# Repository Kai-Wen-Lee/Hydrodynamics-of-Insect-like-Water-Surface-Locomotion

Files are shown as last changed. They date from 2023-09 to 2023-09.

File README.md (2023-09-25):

# Hydrodynamics of Insect like Water Surface Locomotion
 Repository for the Experimental Rig of IP: Design of an experimental set-up for research into the hydrodynamics of insect-like water surface locomotion
 
 - Individual Project Author:             James Maybey   (jdm1g20@soton.ac.uk)
 - PIC for Assembly of Experimental Rig:  Kai            (kwl1y19@soton.ac.uk)
 - Supervisor:                            Swathi Krishna (s.b.krishna@soton.ac.uk)

Current status:
 - Experimental rig nearing completion

Future work:
 1. Find better approach to achieve sinusoidal motion
 2. Fabricate additional 'platform' to ensure outer rod is straight
 3. Swap flexible couplers for solid couplers

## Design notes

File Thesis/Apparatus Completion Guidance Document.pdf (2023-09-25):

## Honeybee surface locomotion flapping arm apparatus:

This document is to help guide the completion of the IP Project Apparatus I designed and

commenced manufacturing. This will outline the remaining tasks and machining, required

components and assembly order.

The creation of this document has flagged up several issues I was not yet aware of, and

was additionally made in haste as to try not delay progress any further. If any questions

arise you feel I can help with, I can try my best to assist. Contact me with the details

below:

James Maybey, Student Email: jdm1g20@soton.ac.uk, (email or teams),

Personal email: jamesmaybey@hotmail.co.uk

I do not have all the details of these tasks figured out, and they will likely require personal

judgement to resolve.

Reading the Assembly order may help understand how all the components were intended to

fit together.

List of components (Before additional work):

- 2 x stepper motors (STM-23S-3RE)
- 2 x Serial adapter/data converter (ES-U-3001-M)
- 1 x Ruland Jaw Coupler Set (10mm bore Jaw 33mm Outer Diameter, 12mm bore Jaw

33mm ODs, 33mm OD rubber spacer)

- 1 x Small pulley 12-tooth (bore at 6.5mm needs fixing method added – set screw?)
- 1 x large pulley 48-tooth with 1 x locking bush 30mm Inner Diameter
- 1 x Toothed belt
- 1 x Plywood mounting board
- Inner shaft (10mm Diameter)
- Outer Shaft (30mm outer diameter -NEEDS CHANGE-, 24 inner diameter) w/ welded

additional mounting cylinder (50mm OD, 4 x M6 mounting holes)

- Mechanism block (Aluminium)
- Wing axle w/ wire slot
- Axle retention ring/cap (21mm ID, mm OD)
- Axle-to-sensor backplate coupler/sleeve (21mm ID, mm OD)
- Sensor back plate (NEEDS ALTERATION/REMANUFACTURING)
- 2 x ball bearings (10mm ID, 26mm OD)
- 1 x ATI NANO17 IP68 (using 3 x M2 screw mounting, no alignment pins)
- 1 x acrylic wing (34mm x 107mm)
- 1 x 3D printed wing adapter/holder (may need redesign/printing)
- 1 x 16-tooth bevel gear (10mm ID, + set screw)
- 1 x 24-tooth bevel gear (21mm ID, + set screw)

- 1 x flange shaft bearing (30mm Bore)
- 1 x Aluminium shaft flange plate (Mounts to Outer shaft with 4 x M6)
- 1 x gearbox Mounting plate (Mounts to gearbox with 4 x M5)
- 4 x Metal Standoffs/spacers (mounts the flange plate and gearbox mounting plate

together with M6)

- 1x Gearbox compatible with stepper motor
- + Fixings

One of the first things that needs to be done is check the mounting of the gears in

respect to the holes bored in the block. The spacing was based on the distances

specified by the manufacturers however I never got to test these aligned in the received

components. If these do not align the block or gears may need

redesigning/manufacturing and this could be a huge problem and setback. The gears

may want a few millimetres taken off the base anyway to stop them being positioned

against the aluminium block and increasing friction.

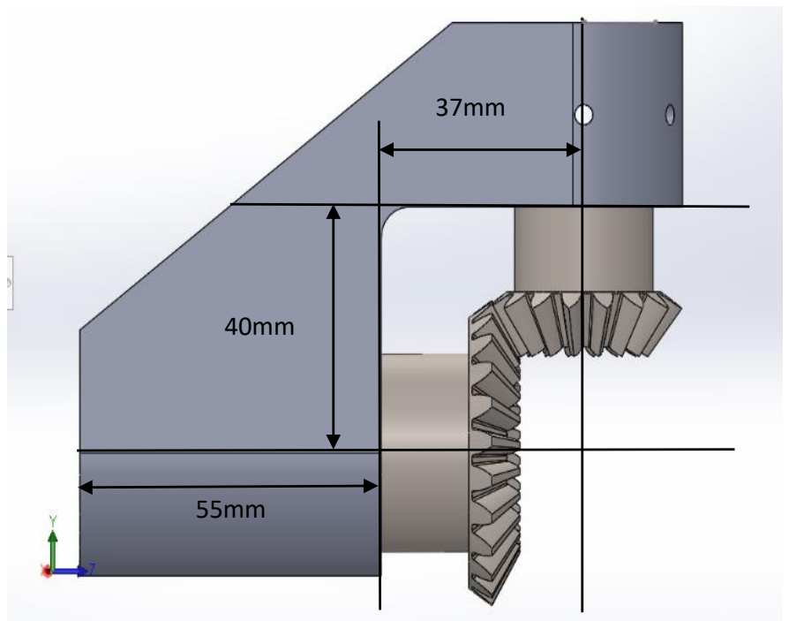
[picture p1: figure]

Tasks to be completed:

- 1. Collect Components from EDMC (if not already done so) – EDMC was to make

the bores of the ‘24-tooth bevel gear’, ‘axle retention ring’ and ‘axle-to-sensor

plate coupler/sleeve’ to 21mm, this is to ensure the 20.1mm sensor can pass

through inside. The EDMC was also supposed to machine the inner diameters of

the Outer shaft to 26mm (from 24mm) to a minimum depth of 8mm on both

ends (this is to hold the alignment bearings)

- 2. The outer shaft OD needs to be reduced on a lathe from 30mm diameter

downwards until it can pass into the 30mm bore of the flange bearing, this is

only required on the longer length of the shaft below the additional welding

piece.

- 3. Get a 700mm length of aluminium 10mm diameter rod (inner shaft) from the

EDMC, may require a material order as they did not have stock when I checked.

This can then be cut to final length during assembly (expected closer to 640mm).

The inner shaft may need its diameter reduced to pass through the 10mm ID

bores of the Alignment bearings and the 16-tooth bevel gear. (Making sure the

10mm Ruland jaw will still have a solid connection/grip)

- 4. The serial adapters need to be positioned and mounted appropriately.

(availability of this part in the labs is questionable so ordering the component

may be necessary). Wiring also needs to be arranged with wires long enough to

run into the tank and between components (Electronics workshop on highfield

campus can help with this).

- 5. The Stepper Motors need to be coded for a sinusoidal motion with 1Hz

frequency resulting in angles of attack between ±45°. For further motion

requirements, discuss with Swathi Krishna. (Wiring also needs to be arranged)

(Ben may be able to assist with Coding)

- 6. A mounting frame needs designing and creating with the available lengths in

Building 185 that is compatible with the Tank and mounting plate and positions

the wing at a suitable depth.

- 7. Alter/Remanufacture/Redesign Sensor Back plate, The current back plate is

compatible with the standard Nano17 model however the IP68 submergible

model has different mounting arrangements and so this needs a new piece or

alterations. An example suitable design has been provided. This can be used if

deemed suitable.

- 8. The 3D printed Wing adapter that holds the acrylic wing may require

redesigning and reprinting if the mounting holes for M2 screws do not align with

new sensor and also aren’t positioned for easy assembly.

- 9. Check wing size gives an estimate torque reading that does not exceed the

rating of the sensor. If not Lasercut new wing to new chosen design – Discuss

with Swathi Krishna.

- 10. If alignment bearings don’t stay in the outer shaft with a pressure fit, add an

additional method of retention.

- 11. Where deemed applicable and possible add countersinks if time permits.
- 12. During assembly it may be found the ‘Axle coupler/sleeve’ needs to be

machined to a shorter length if the bevel gear and coupler interact.

- 13. Make the jaw couplers support axial load

- 14. Add set screw to small pulley/ make shaft extension+coupler

Task 1:

‘Collect Components from EDMC (if not already done so) – EDMC was to make the bores of

the ‘24-tooth bevel gear’, ‘axle retention ring’ and ‘axle-to-sensor plate coupler/sleeve’ to

21mm, this is to ensure the 20.1mm sensor can pass through inside (aluminium block has

20.5mm hole). The EDMC was also supposed to machine the inner diameters of the Outer

shaft to 26mm (from 24mm) to a minimum depth of 8mm on both ends (this is to hold the

alignment bearings)’

Technical drawings shown below highlighting the mentioned changes referred to.

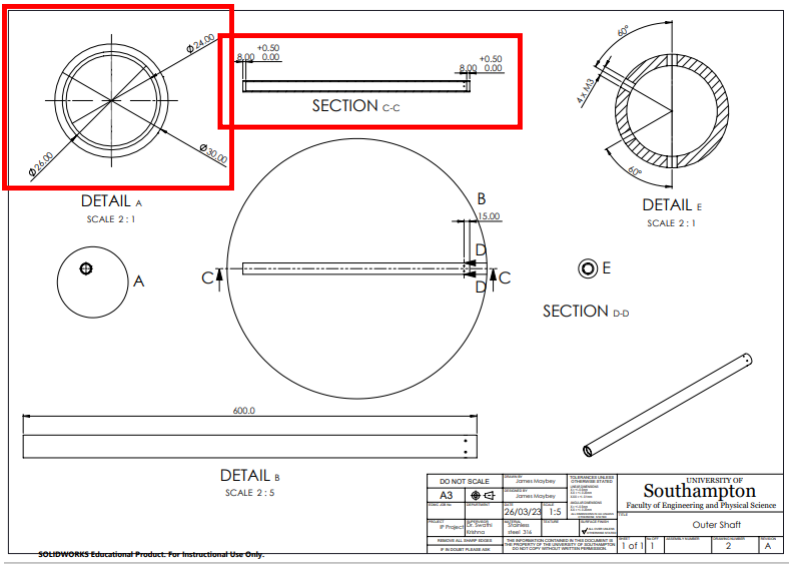
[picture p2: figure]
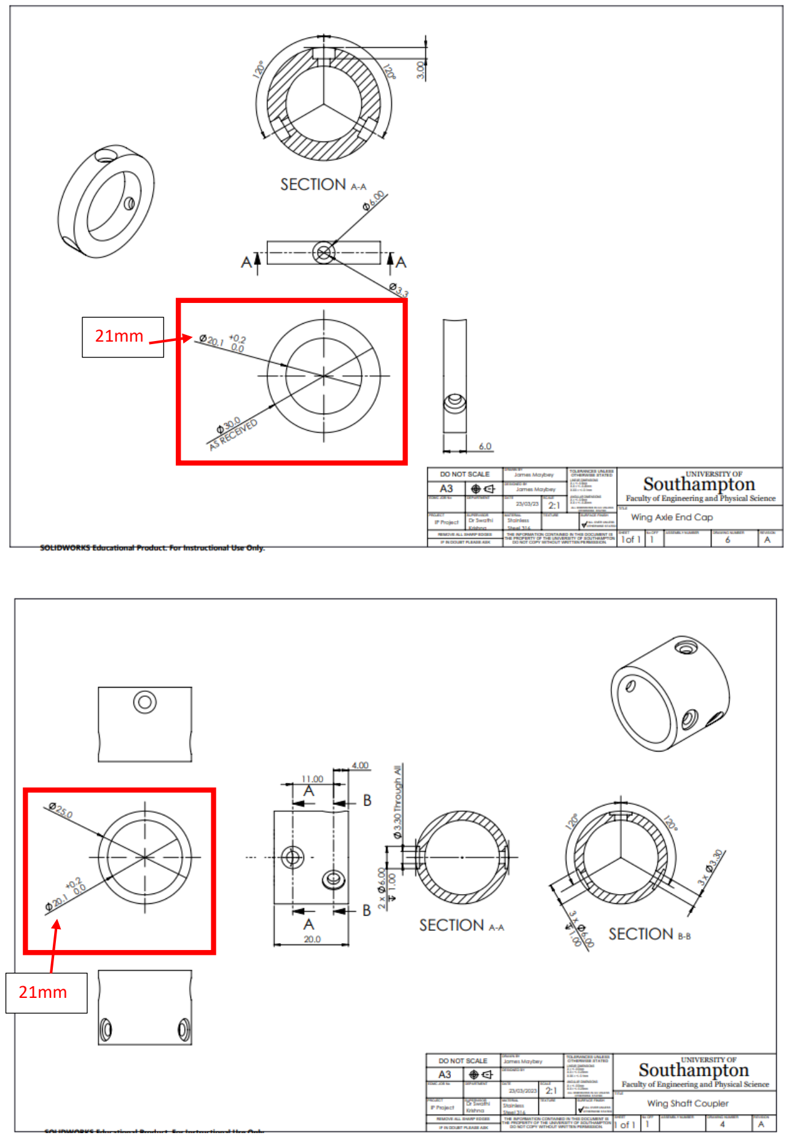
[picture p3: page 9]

21mm

21mm

Task 2:

‘The outer shaft OD needs to be reduced on a lathe from 30mm diameter downwards until

it can pass into the 30mm bore of the flange bearing, this is only required on the longer

length of the shaft below the additional welding piece.’

Technical drawings of Outer shaft assembly and flange bearing with areas of change

highlighted.

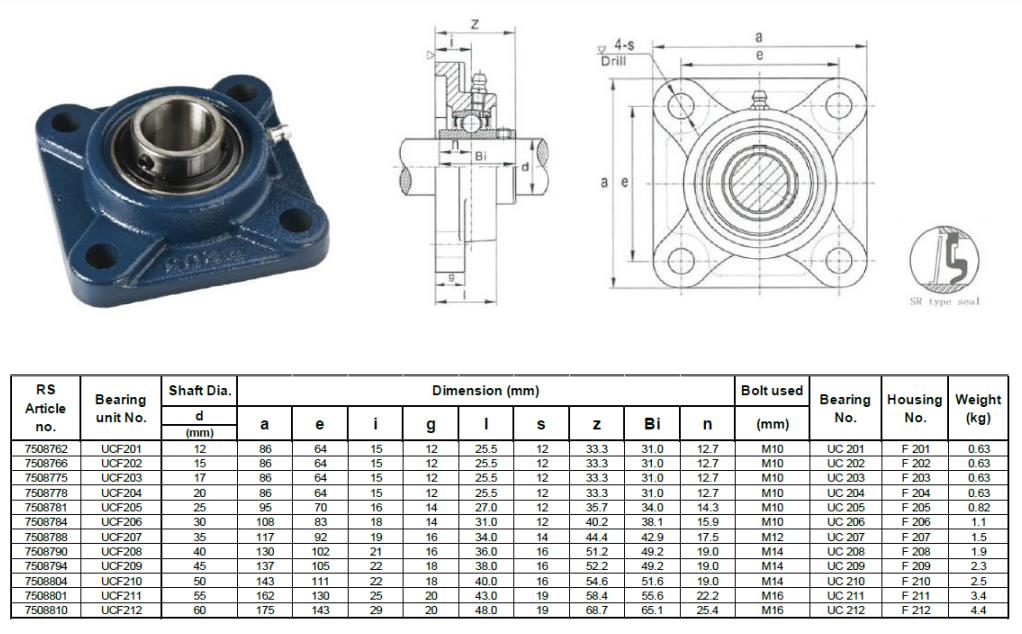
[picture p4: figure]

^^^Using 30mm shaft diameter size (d)^^^

Task 3:

‘Get a 700mm length of aluminium 10mm diameter rod (inner shaft) from the EDMC, may

require a material order as they did not have stock when I checked. This can then be cut to

final length during assembly (expected closer to 640mm). The inner shaft may need its

diameter reduced to pass through the 10mm ID bores of the Alignment bearings and the 16-

tooth bevel gear. (Making sure the 10mm Ruland jaw will still have a solid connection/grip)’

Drawings of inner shaft and alignment bearings assembly.

Rough estimate

Task 4:

‘The serial adapters need to be positioned and mounted appropriately. (availability of this

part in the labs is questionable so ordering the component may be necessary). Wiring also

needs to be arranged with wires long enough to run into the tank and between components

(Electronics workshop on highfield campus can help with this).’

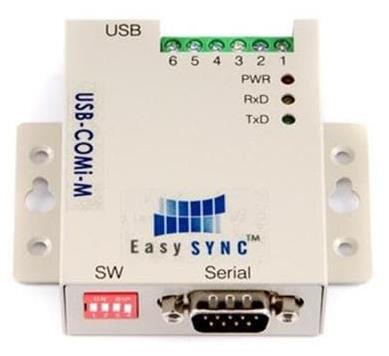
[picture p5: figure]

ES-U-3001-M USB-to-Serial data converter

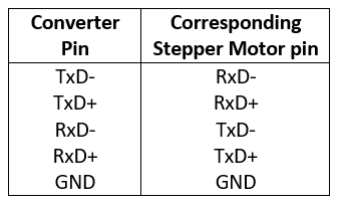
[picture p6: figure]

Wiring guide between converter and stepper motor

The switches on the converter should display S1,2 and 4 ON and S2 OFF, using this table

below as guide.

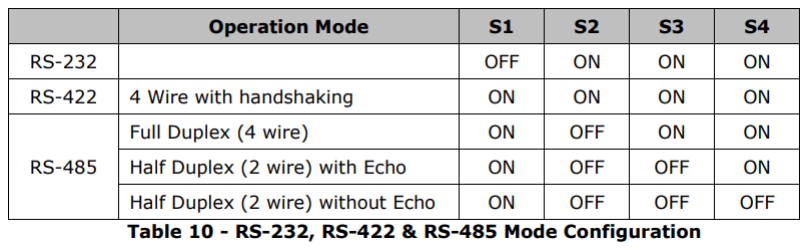
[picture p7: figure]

Task 5:

‘The Stepper Motors need to be coded for a sinusoidal motion with 1Hz frequency resulting

in angles of attack between ±45°. For further motion requirements, discuss with Swathi

Krishna. (Wiring also needs to be arranged) (Ben may be able to assist with Coding)’

Link to control codes and documentation

Useful links for setup and coding:

https://appliedmotion.s3.amazonaws.com/920-0020F_STM23_24_S_Q_QuickSetup.pdf

https://www.applied-motion.com/s/product/integrated-

drivemotorstm23s3re/01t5i000000xylkAAA (https://www.applied-motion.com/s/product/integrated-drivemotorstm23s3re/01t5i000000xylkAAA)

https://appliedmotion.s3.amazonaws.com/Host-Command-Reference_920-0002W_0.pdf

Task 6:

‘A mounting frame needs designing and creating with the available lengths in Building 185

that is compatible with the Tank and mounting plate and positions the wing at a suitable

depth.’

Mounting board technical drawing and example image of mounting, can also look at Ben’s

cyclorotor for example.

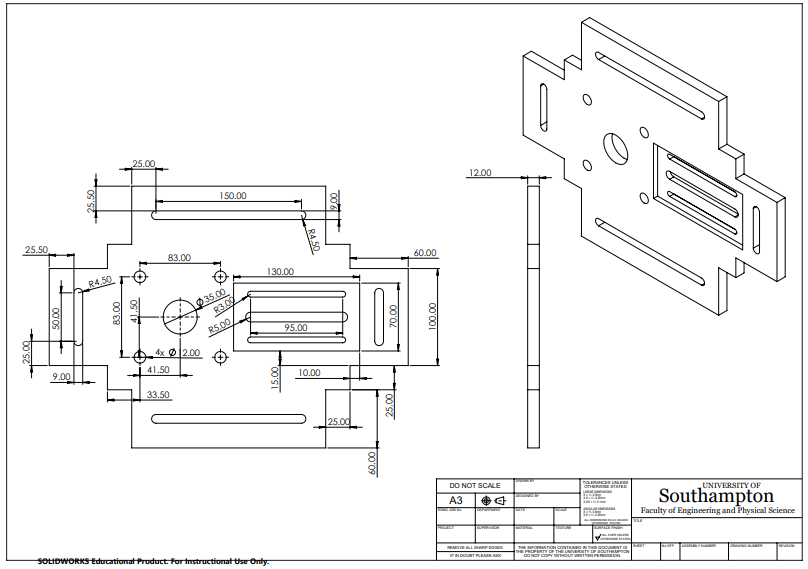
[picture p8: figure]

Mounting board dimensions, Suitable for M8 bolts to secure to framework

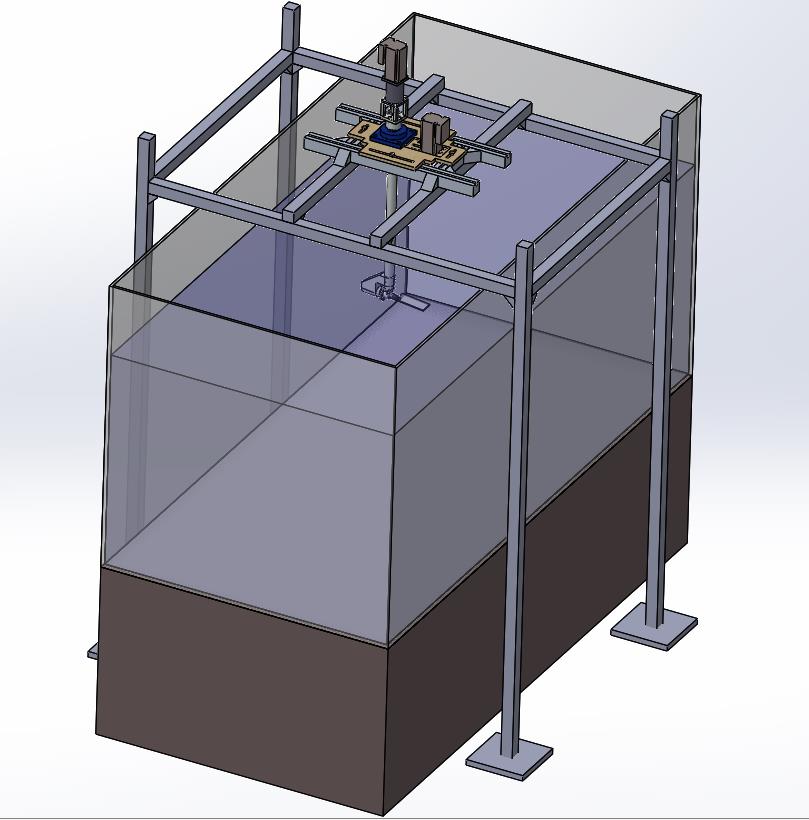
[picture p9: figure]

Example mount structure, does not need to be followed

Task 7:

‘Alter/Remanufacture/Redesign Sensor Back plate, The current back plate is compatible

with the standard Nano17 model however the IP68 submergible model has different

mounting arrangements and so this needs a new piece or alterations. An example suitable

design has been provided. This can be used if deemed suitable.’

Existing plate (photo of final look, +countersinks, -thread in side M3 holes)(drawings from

EDMC order of existing plate):

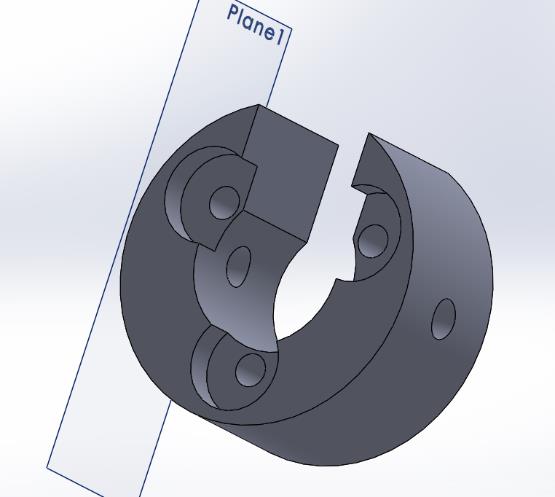
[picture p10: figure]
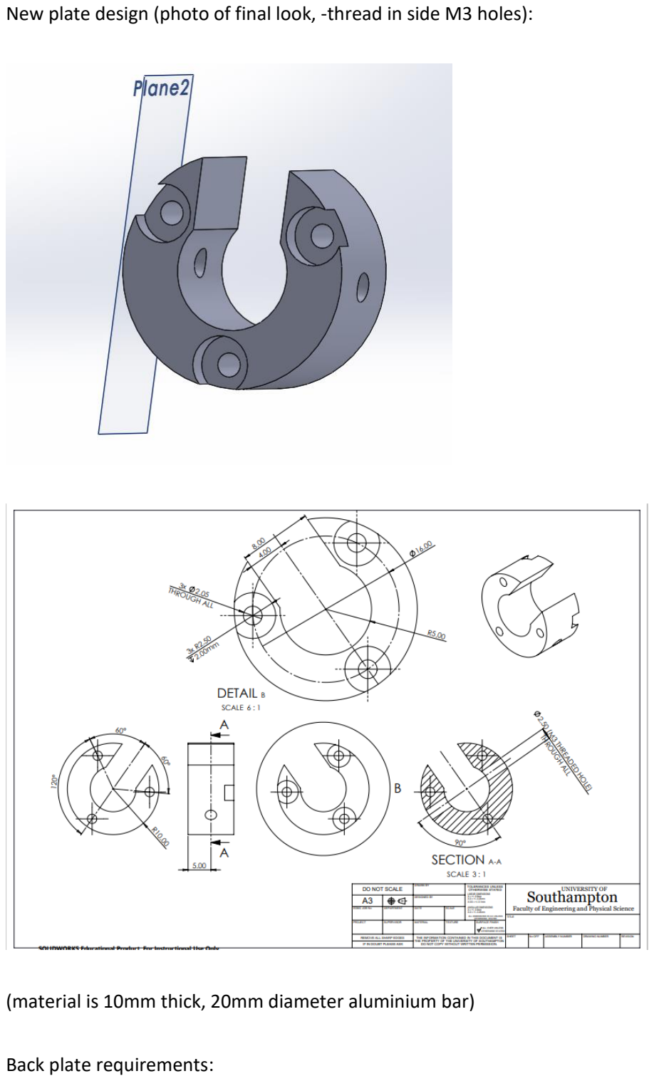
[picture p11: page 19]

New plate design (photo of final look, -thread in side M3 holes):

(material is 10mm thick, 20mm diameter aluminium bar)

Back plate requirements:

Diameter ~20mm, ATI sensor wire slot and hole suitable for the axial cable, 3x M2 clearance

mounting/interface holes, 2 x Connecting M3 threaded holes for sensor-to-axle coupler,

Countersinks to keep screw head flush or beneath outerface.

Reducing the backplate to 9.5mm length instead of 10mm allows for further assembly

tolerance.

CONSIDER SCREW HEAD SIZE, IF THEY EXCEED OVER THE EDGE IN THE COUNTERSINKS, THE

PART MAY NOT FIT INSIDE THE COUPLER, SOLUTIONS: SCREW HEADS COULD BE

MACHINED AWAY, OR DESIGN REWORKED

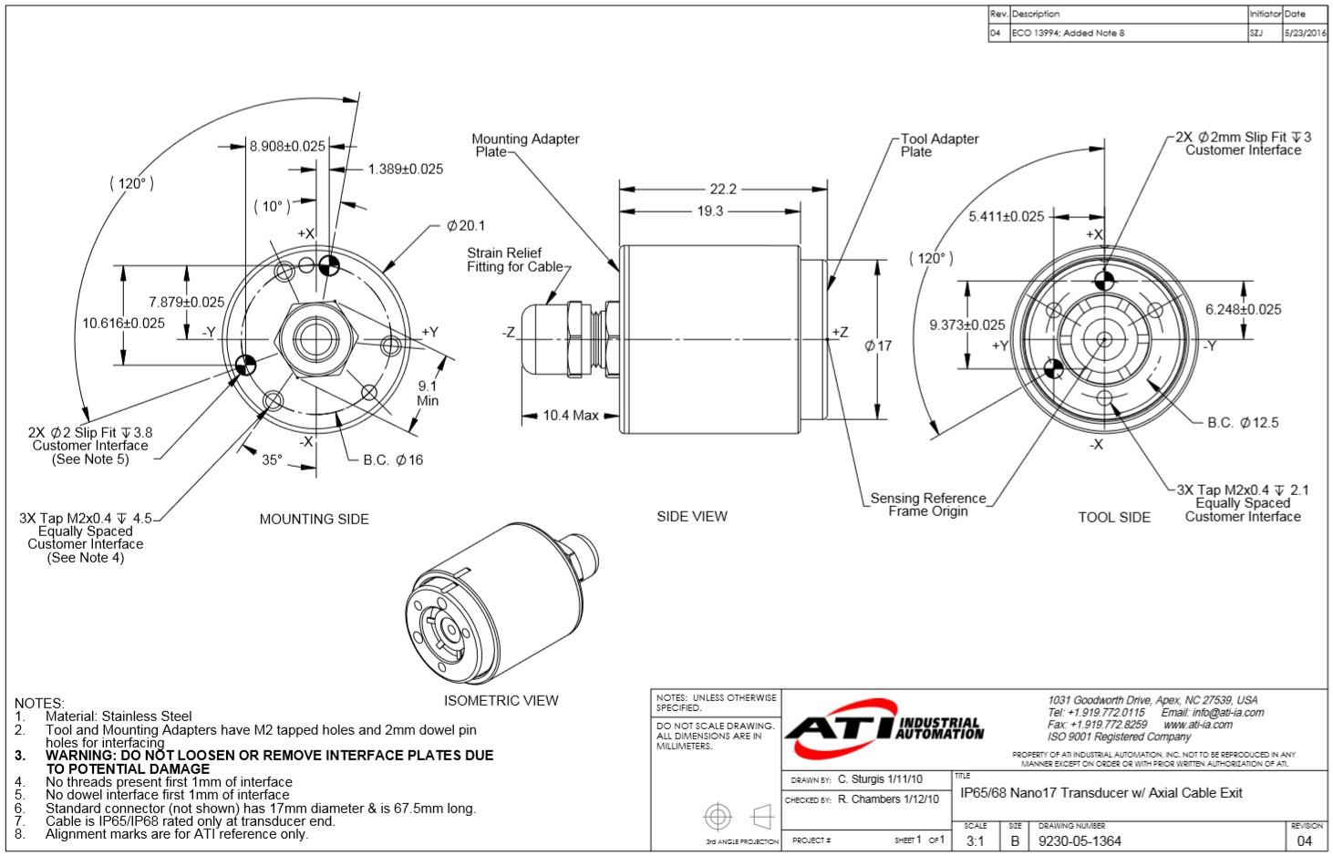
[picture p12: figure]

Task 8:

‘The 3D printed Wing adapter that holds the acrylic wing may require redesigning and

reprinting if the mounting holes for M2 screws do not align with new sensor and also aren’t

positioned for easy assembly.’

Current 3D print problems:

Difficulty screwing in 3x M2 fixing screws

Fixing interface shown below

Requirements:

3x M2 screw interface clearance holes with countersinks, centres on 12.5mm circular

arrangement 120 Degrees apart

Two pronged forks with semi circular profile to hold plastic wing (current design uses

2.05mm max thickness prongs with 10mm length.)

Task 9:

‘Check wing size gives an estimate torque reading that does not exceed the rating of the

sensor. If not Lasercut new wing to new chosen design – Discuss with Swathi Krishna.’

Swathi was to check the calculations to make sure the torque on the wing did not exceed

the sensors max torque. If change is required arrange measurements with Swathi and laser

cut replacement.

Wing plate should be positioned with the forks at a quarter chord length from the leading

edge, shown below.

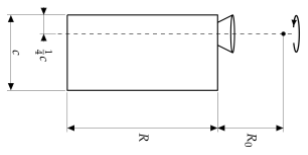
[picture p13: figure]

Current wing size 34mmx107mm, 3mm thickness clear acrylic

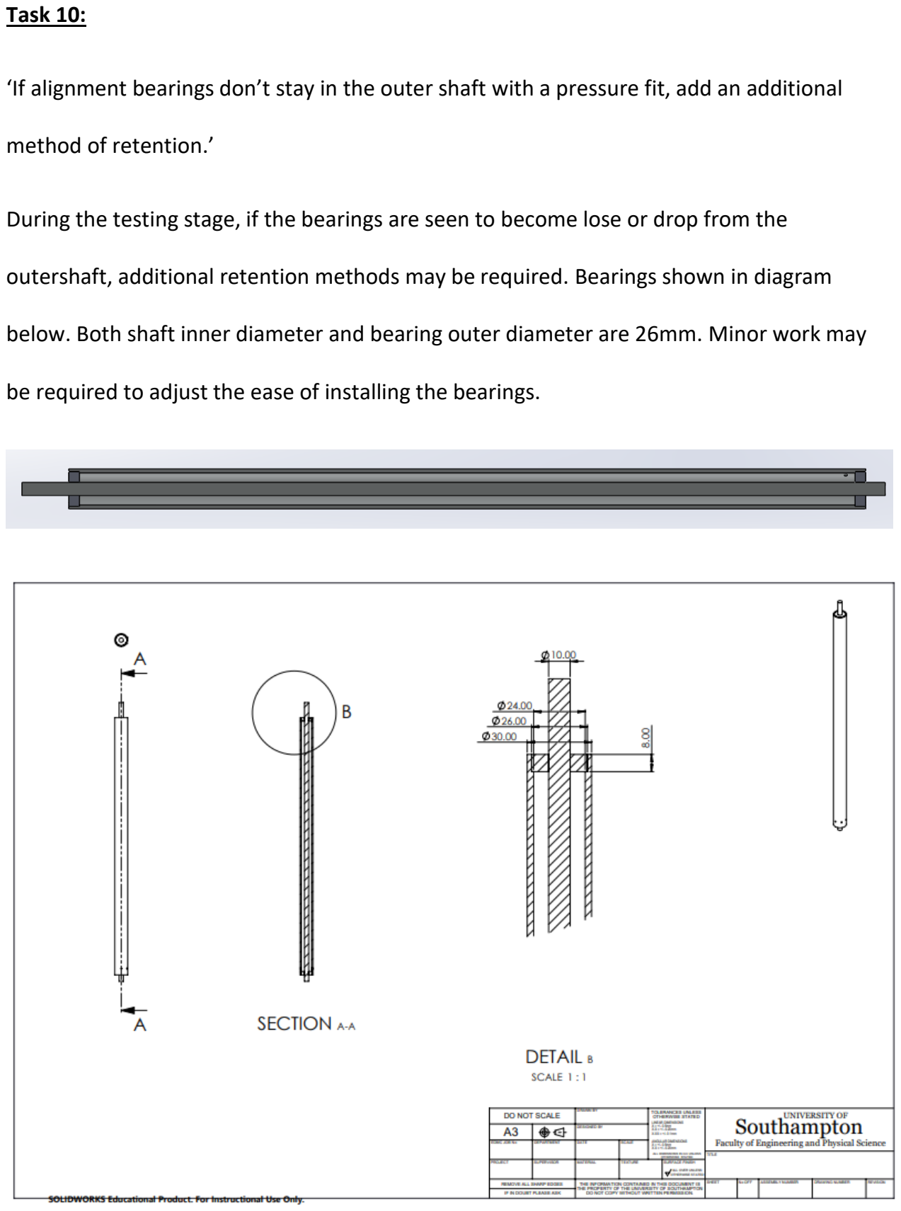
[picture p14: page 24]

Task 10:

‘If alignment bearings don’t stay in the outer shaft with a pressure fit, add an additional

method of retention.’

During the testing stage, if the bearings are seen to become lose or drop from the

outershaft, additional retention methods may be required. Bearings shown in diagram

below. Both shaft inner diameter and bearing outer diameter are 26mm. Minor work may

be required to adjust the ease of installing the bearings.

Task 11:

‘Where deemed applicable and possible add countersinks if time permits.’

Countersinks can be added to components if size and material width permits, e.g axle

retention ring.

WARNING: With the inner bore increased to 21mm by the EDMC, the remaining material

is reduced for counterbore depth

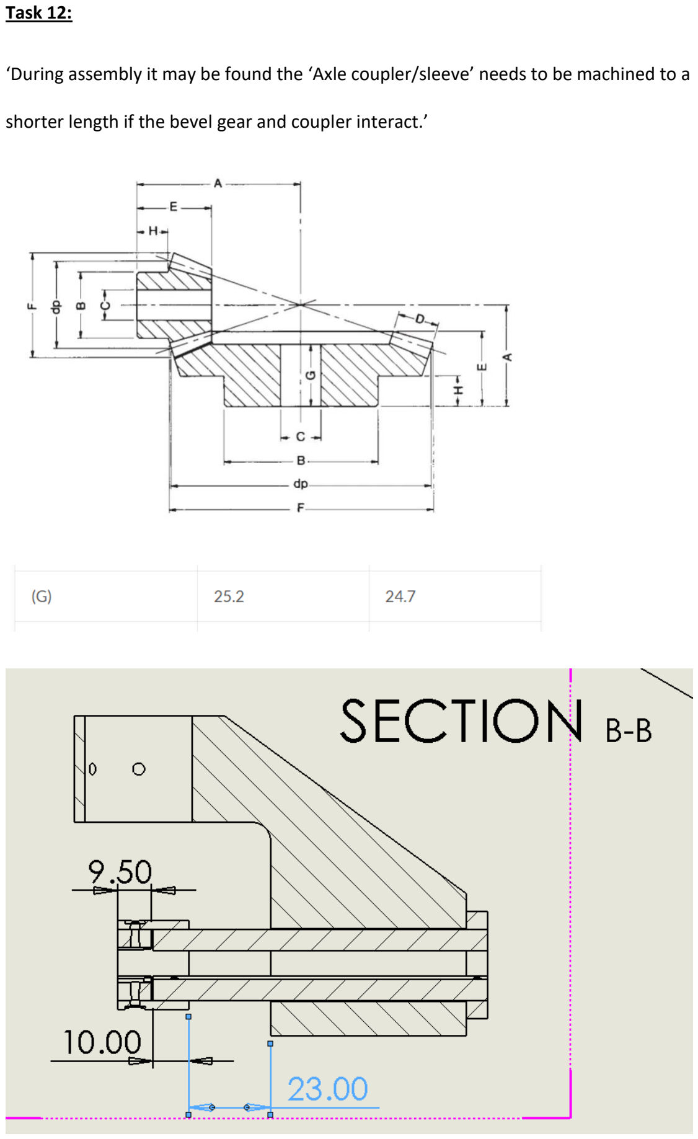
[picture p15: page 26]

Task 12:

‘During assembly it may be found the ‘Axle coupler/sleeve’ needs to be machined to a

shorter length if the bevel gear and coupler interact.’

Design currently leaves 23mm space for 24.7mm long gear (Measurement specified by

manufacturers site, Not measured from received component).

There are 3 options to change this:

- Machine the Gears front face (where the teeth are) back, however make sure to try

not to interfere with gear meshing

- Machine the coupler back however this will start to near the 3x M3 clearance holes
- Produce a new, longer, axle that will increase this space (Simplest fix but most

effort and cost)

Task 13:

‘Make the jaw couplers support axial load’

I was made aware that there was a way to further manufacture onto the jaw coupler to

allow the coupler to support load axially (to not pull apart at the rubber spacer). I am unsure

whether this will be required as the attached driving gear will fall against the 2nd gear and

this may permit operation.

I am not sure how this change to the coupler is done as I never got round to investigating

myself but I believe I was instructed to speak to Building 185 Technician Sam Harper.

Task 13:

‘14. Add set screw to small pulley/ make shaft extension+coupler’

Due to the bolts that hold the flange bearing in place, the pulley may need to be positioned

lower on the outer shaft. To achieve correct alignment, the small pulley may need to be

fixed to another shaft that couples to the motor. The motor has 6.35mm output shaft

diameter whilst the pulley has a 6.5mm drilled bore.

By adding a 1 or 2mm set screw to the neck of the small (12-tooth) pulley, it can be fixed

to a 6.5mm shaft and then coupled to the motor. This Coupler will need to be bought or

made.

Assembly:

Step No. | Step | Components involved | Instructions
1 | Fix the outer shaft | Welded outer shaft subassembly, Mounting frame, Plywood mounting board, Flange bearing | Fix the flange bearing to the board and the board to the frame with M10 and M8 bolts, then push the outer shaft through the bearing and tighten set screws.
2 | Insert inner shaft and bearings | Inner shaft, alignment bearings x2, outer shaft | Push the inner shaft down the outer shaft and place the alignment bearings over the inner shaft and into the ends of the outer shaft
3 | Fix the pulley system | Large pulley, small pulley, locking bush, pulley belt, stepper motor | Slide the large pulley and bush onto the outer shaft from underneath and tighten the set screws to fix, then place motor onto the board and use set screw to fix the small pulley onto the shaft, then use 4 M4 machine screws to bolt the motor into position whilst tightening the belt in place.
4 | Fix the second motor | Gearbox, motor, gearbox plate, outer shaft plate, standoffs x4, Ruland jaw coupler | Bolt the shaft plate onto the welded sleeve on the top of the outer shaft using 4 M6 bolts, then secure the 4 standoffs to this plate with 4 more M6 bolts, secure the motor to the gearbox using 4 M5 machine screws and then bolt the gearbox to its plate with 4 M5 bolts, this plate can then lastly be secured to the standoffs with M6 bolts at the same time the Ruland jaw coupler is aligned and fixed to the inner shaft and gearbox output
5 | Create the gear sub assembly | Mechanism block, retention ring, Nano17, sensor back plate, 21mm bore gear, wing axle, coupling sleeve | Firstly, pass the sensor through the retention ring, mechanism block, 21mm bore gear, and coupling sleeve. Then slot the back plate over the sensors wire and fix the backplate to the back of the sensor with M2 screws, then slot the wing axle over the wire and slide into place. Then using M3 screws, fix the sleeve to the back plate and wing axle, then slot the wing axle through the gear and mechanism block and fix to the retention ring with M3s, finally tighten the 24-tooth gear’s set screw to fix into the wing axle.
6 | Fix the wing to the sensor | Wing adapter, wing plate | Glue the wing plate into position in the adapter, then screw the adapter onto the sensor using M2 screws
7 | Fix the gear sub assembly onto the outer shaft | 16-tooth driving gear | Putting the driving gear into its final position next to the driven gear allows for the assembly to be slid onto the bottom of the outer shaft and the inner shaft can pass into the driving gear whilst the outer shaft stays in the mechanism block, the set screw can then be tightened, fixing the gear, and the 4 M3 machine screws can be used to fix the mechanism block onto the outer shaft
8 | Mount the apparatus | Testing environment | The mounting frame can then be fixed to the existing frame above the tanks using right-angled brackets
9 | Fix the electronics | Wire connections, signal converter (serial adapter) | The wiring can then be implemented, from power source to motors and from signal generator to the converters and then also to the motors. The sensor wire can also then be connected into the reading device, signal converters can be screwed onto the wooden board for fixing if space permits.

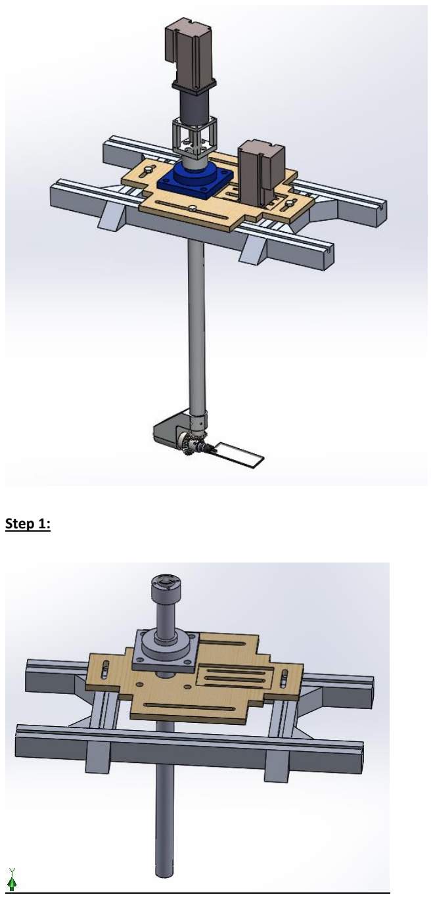
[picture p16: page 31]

Step 1:

Step 2:

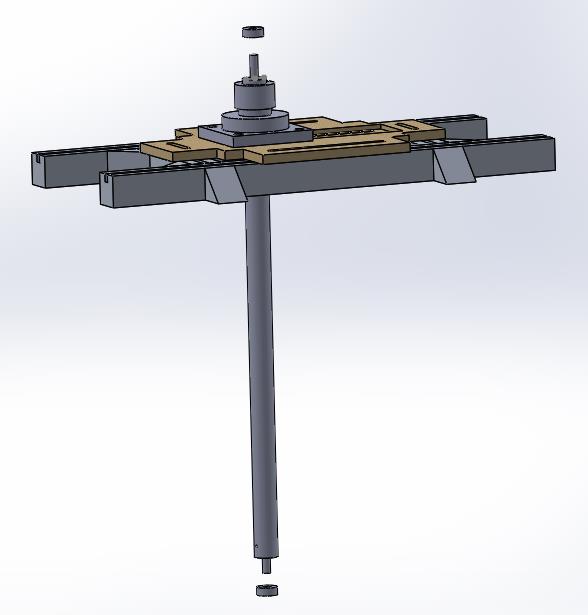
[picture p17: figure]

Step 3:

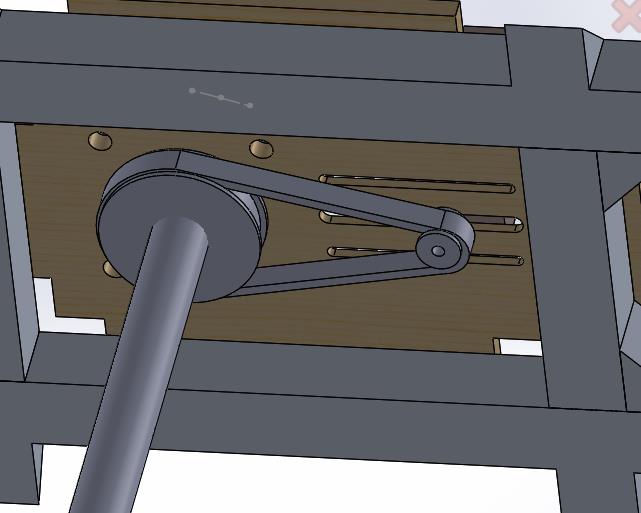
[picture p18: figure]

This step does not show the additional shaft/coupler that will likely be needed. Image

shows how belt is close to the flange bearing mounting holes.

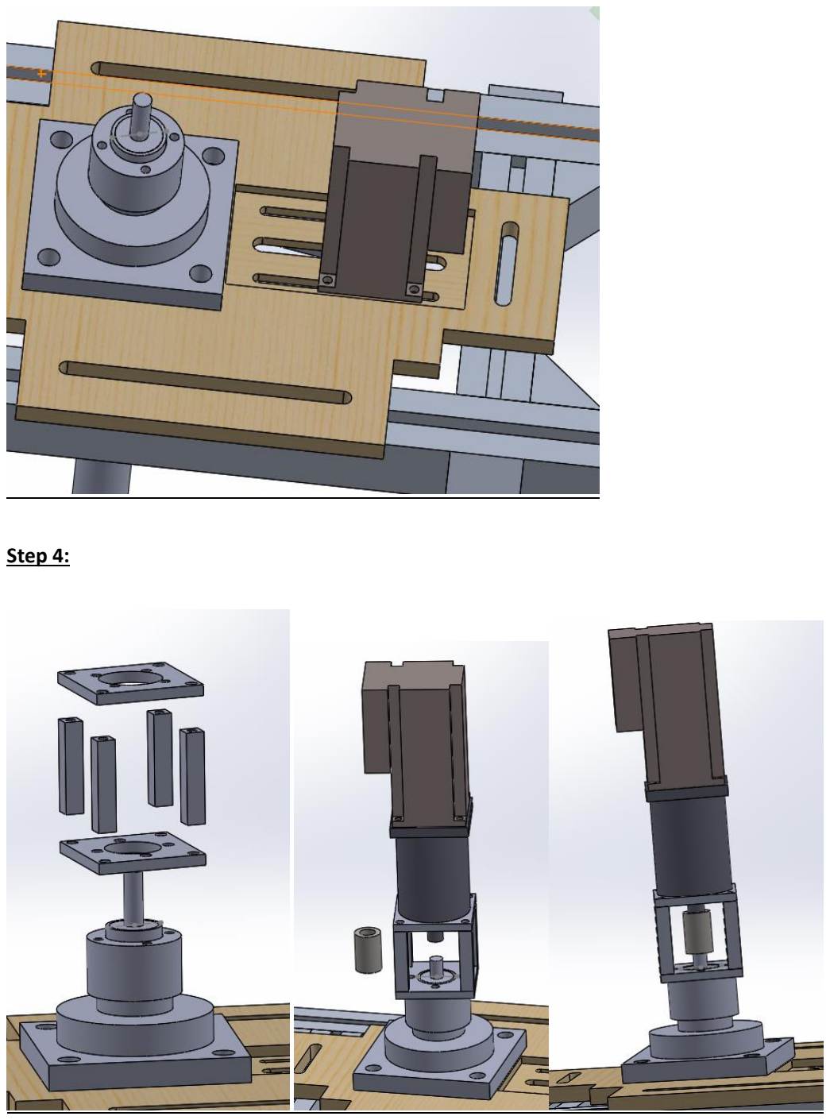
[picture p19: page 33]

Step 4:

Step 5:

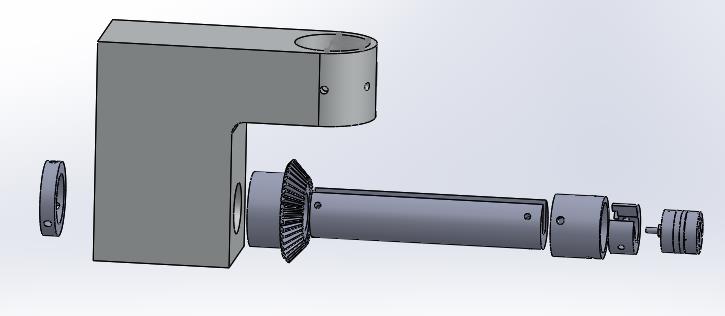
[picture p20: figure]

Due to the sensors axial cable, it will need to pass through the bores of the end ring,

aluminium block,24-tooth gear, and coupler

Step 6:

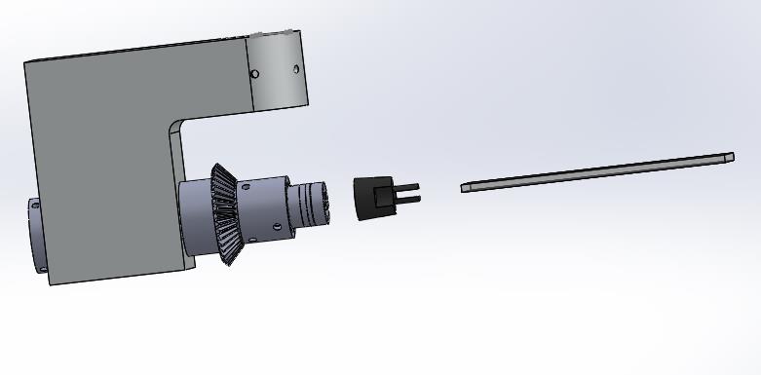
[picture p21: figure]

(Gears not accurate – shown gear corresponds to 24-tooth gear)

Step 7:

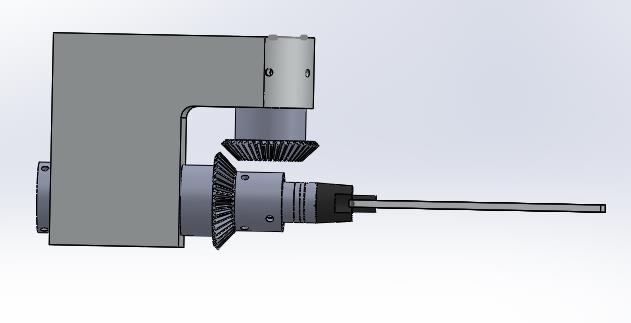
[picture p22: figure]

(Gears not accurate – New gear in photo corresponds to 16-tooth gear)

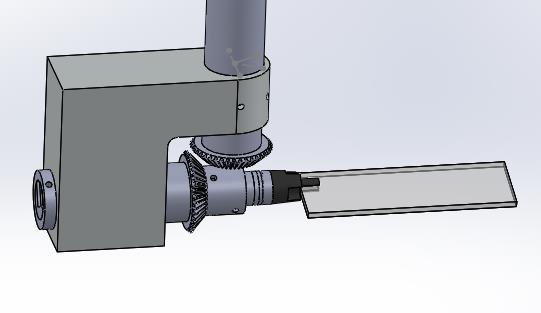
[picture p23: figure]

Slide both parts pre-positioned up onto the bottom of the outer and inner shaft

Step 8:

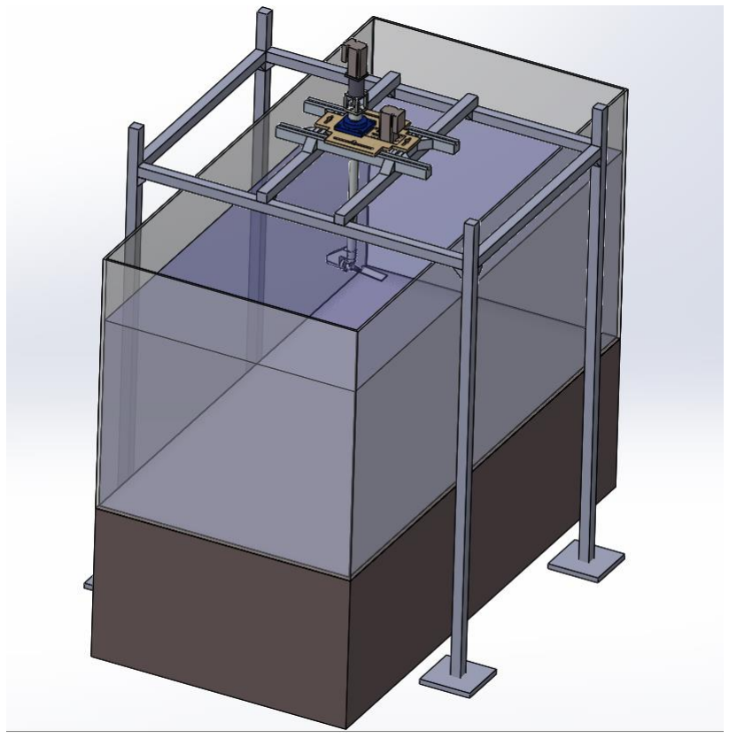
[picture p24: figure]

Step 9:

Fix Electronics

More Useful links:

https://www.applied-motion.com/s/product/detail/01t5i000000xylkAAA?name=STM23S-

3RE-NEMA-23-Integrated-Drive-Motor-w-Encoder (https://www.applied-motion.com/s/product/detail/01t5i000000xylkAAA) – Stepper motor

https://simplybearings.co.uk/shop/p20194084/P12-5M-15F-5mm-Pitch-12-Tooth-Flanged-

HTD-Type-Steel-Timing-Pulley-for-15mm-Wide-Belts/product_info.html (https://simplybearings.co.uk/shop/p20194084/P12-5M-15F-5mm-Pitch-12-Tooth-Flanged-HTD-Type-Steel-Timing-Pulley-for-15mm-Wide-Belts/product_info.html) - small pulley

https://simplybearings.co.uk/shop/p671275/HTD425-15-85-Major-Brand-Synchronous-Belt-

15mm-Wide-5mm-Pitch-85-Teeth/product_info.html (https://simplybearings.co.uk/shop/p671275/HTD425-15-85-Major-Brand-Synchronous-Belt-15mm-Wide-5mm-Pitch-85-Teeth/product_info.html) - Pulley belt

https://simplybearings.co.uk/shop/p20193090/TL48-5M-15F-5mm-Pitch-48-Tooth-Flanged-

HTD-Type-Steel-Taper-Bore-Timing-Pulley-for-15mm-Wide-Belts/product_info.html (https://simplybearings.co.uk/shop/p20193090/TL48-5M-15F-5mm-Pitch-48-Tooth-Flanged-HTD-Type-Steel-Taper-Bore-Timing-Pulley-for-15mm-Wide-Belts/product_info.html) - large

pulley

https://simplybearings.co.uk/shop/p552040/1210-30-Tapered-Locking-Bush-with-30mm-

Bore/product_info.html (https://simplybearings.co.uk/shop/p552040/1210-30-Tapered-Locking-Bush-with-30mm-Bore/product_info.html) -large pulley locking bush

https://uk.rs-online.com/web/p/ball-bearings/6189991 - ball bearing

https://bepltd.com/products/2-mod-1-5-ratio-16-24-teeth-precision-bevel-gears-steel-en8 -

bevel gear pair

https://uk.rs-online.com/web/p/bearing-units/7508784 - flange bearing

https://uk.rs-online.com/web/p/flexible-couplings/4231775 - 12mm gearbox jaw for

coupling

https://uk.rs-online.com/web/p/flexible-couplings/7019155 - coupling rubber spacer

https://uk.rs-online.com/web/p/flexible-couplings/4231769 - 10mm inner shaft jaw for

coupling https://motioncontrolproducts.com/media/productattach/r/e/re-planetary-gearbox.pdf -

gearbox dimensions (RE55 model for Nema 23)

https://www.ati-ia.com/products/ft/ft_models.aspx?id=Nano17+IP65%2fIP68 – ATI Nano17

IP68 Web page (useful documents for sensor found here)

https://uk.rs-online.com/web/p/standoffs/1768297 - Metal female-female standoffs

(unsure if these are the exact ones)

https://www.mouser.co.uk/ProductDetail/Connective-Peripherals/ES-U-3001-

M?qs=jotIDw4kbYV9GiEaKLbLDA%3D%3D (https://www.mouser.co.uk/ProductDetail/Connective-Peripherals/ES-U-3001-M?qs=jotIDw4kbYV9GiEaKLbLDA%3D%3D) – Serial adapter/data converter, Data sheet can

be found here

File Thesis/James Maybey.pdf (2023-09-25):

a

# Design of an experimental set-up for research into

# the hydrodynamics of insect-like water surface

# locomotion

## James Maybey

18/05/2023

## Dr. Swathi Krishna, Desmond Lim

## Word Count: 10,499

## Pages: 70

## This report is submitted in partial fulfilment of the requirements for the

## Mechanical Engineering with Automotive Engineering, Faculty of

## Engineering and Physical Sciences, University of Southampton

i

## Decleration:

I, James Maybey declare that this thesis and the work presented in it are my own and has been generated by me as the result of my own original research.

I confirm that:

1. This work was done wholly or mainly while in candidature for a degree at this University;
2. Where any part of this thesis has previously been submitted for any other qualification at this University or any other institution, this has been clearly stated;
3. Where I have consulted the published work of others, this is always clearly attributed;
4. Where I have quoted from the work of others, the source is always given. With the exception of such quotations, this thesis is entirely my own work;
5. I have acknowledged all main sources of help;
6. Where the thesis is based on work done by myself jointly with others, I have made clear exactly what was done by others and what I have contributed myself;
7. None of this work has been published before submission.

James Maybey

ii

### Acknowledgements:

I thank my supervisor Dr. Swathi Krishna for supporting my work and giving me guidance

during my project. I also am grateful for being given the opportunity to work on this

project by Dr. Krishna. I further thank Desmond Lim for offering his additional time and

support on this project. I lastly thank my Father for helping me and giving me the

motivation to continue with my work.

iii

### Abstract:

Many studies have been made over time into the motion employed by insects’ wings.

The latest motions to be studied need to be replicated and analysed by employing an

experimental apparatus. A vast number of set-ups exist with the sole purpose of

recreating the flapping motion of wings, and from these, results can be found and

implemented into robotic application. Unmanned vehicles in both air and water would

benefit greatly from the planned future research. The hydrofoiling of honeybee’s wings

will allow for a great new deal of design possibilities, with existing ideas for

implementation in drone recovery.

This paper outlines the design of an experimental piece of equipment that will allow the

modelling of a wing in a water environment. The equipment will be designed to have both

a pitch and stroke motion, both with independent control systems. The design will be

used for future experimentation in both static and flowing water and this is when the

testing and results data will be collected. The pitching mechanism is controlled with a

pair of bevel gears and outputted from a stepper motor. A second stepper motor will

drive the stroke motion however will use a timing belt pulley system to deliver this output.

The future testing will involve the use of a force-torque sensor that will allow the studying

of related forces experienced throughout the stages of the honeybee’s motion. These

forces can be used to produce useful coefficients and allow for future optimization to

idealise said coefficients.

The design was inspired from existing apparatus outlined in Section 2 of the report

(Background). These existing designs allowed for a stable foundation to develop upon in

an iterative manner.

iv

### Nomenclature:

Angle of attack, α (°)

Area, A (m²
)

Chord length (wing), c (m)

Coefficient of Drag, CD

Coefficient of Lift, CL

Coefficient of Power. CP

Density, ρ (kg/m³
)

Distance to axis of rotation, R0 (m)

Force, F (N)

Frequency, f (Hz)

Span length (wing), R (m)

Torque, T (Nm)

Velocity of free stream flowing fluid (Lab+motion), Uinf (m/s)

Speed of free stream flowing fluid (Lab apparatus speed), Vinf (m/s)

v

### List of Figures:

Figure 2.5: Experimental set-up with exclusively stroke and pitch actuation (pulley)…… 6

vi

vii

### List of Tables:

viii

### List of Abbreviations:

AR: Aspect Ratio

CAD: Computer-Aided Design

Eq: Equation

FEA: Finite Element Analysis

HTD: High-Torque Drive

HUAV: Hybrid Underwater-Aerial Vehicles

ID: Inner Diameter

MAV: Micro Air Vehicle

OD: Outer Diameter

PIV: Particle Image Velocimetry

RWT: Recirculating Water Tunnel

UAV: Unmanned Aerial Vehicle

UAAV: Unmanned Aerial-Aquatic Vehicle

UV: Underwater Vehicle

ix

# Contents:

x

### 1. Introduction:

### 1.1. Big picture:

Honeybee’s have recently been found to use their wings to perform a version of surface

locomotion that involves moving their wings back and forward across the water-air

boundary to create a hydrofoiling effect. This effect means that when the honeybee’s

land on their underside on the water surface they can propel themselves forward and

move towards dry land. Investigating this motion may allow for experimental research to

be made into replicating this motion and then implementing it into mechatronics. With

Unmanned Aerial-Aquatic Vehicles (UAAVs) predominantly using jet-thrust or rotor

propulsion to create their forward motion, this method would exist as a backup system

separate to the primary motion. Jet and rotor propulsion allow reliable and rapid

manoeuvring, capable of leaving and landing on the water surface whereas the

honeybee’s motion will only be applicable to the water surface locomotion. This therefore

narrows the motion’s applicability down to solely aquatic movement, most likely

presenting as a backup recovery motion usable when a UAAV malfunctions and crashes

to the water’s surface.

This project will focus on the design of an experimental apparatus that can model the

sinusoidal motion of the wing and produce measurable values of forces and torques

created by the movement. The forces and torques surrounding the motion will determine

its viability in implementation in the future. The apparatus will also leave the possibility for

future variation and customisation to allow experiments with a variety of wing shapes and

aspect ratios. The design process will include the use of Computer-Aided Design (CAD)

to show the stages of design development and illustrate the decisions made along the

way, this will include the component choices and assembly methods.

### 1.2. Aims and Objectives:

The overall aim of this project is to design and create an apparatus capable of yielding

model results that are relevant and transferable. This comes with project design

constraints like target capabilities (e.g., fine resolution) and also additional limitations like

budgeting. The project will also be broken down into smaller objectives, these include the

deciding of mechanisms that will deliver the motion, the choice of electronic and motion

transmission components and lastly finalising a design that is fully capable of assembly

to process onto manufacture.

### 1.3. Report Structure:

This report will be structured by initially performing research into the existing literature

surrounding the topic. This will allow the ability to outline the expected motion, the methods of modelling, existing apparatus and UAAVs and the potential utility. Following

the literature review, the next area for design constraints come from the location and

environments the apparatus will be testing in. This includes planning through the future

experimentation and methodology to allow for the design to be suitable for fixing to the

lab equipment like static water tanks and water flumes. Using these two rounds of

research it is possible to create a brief specification for what the apparatus aims to

achieve and will be constrained by. From these constraints, beginning with initial

sketching, the developmental design process will start. In this process, design decisions

will be made on the methods of power transmission and how the motion will be delivered.

The final design is summarised and key aspects outlined. This includes the justification

of design decisions along the way, including the components by using investigative

torque calculations to ensure the motors will be capable of delivering the required output.

The electronics that control the system are then outlined and briefly explained. The final

stage includes the manufacturing review, explaining the differences between the planned

design and manufactured rig. The report ends with a conclusion and discussion on the

future work from this project.

### 2. Background:

The purpose of the background chapter is to investigate the existing information

available that has brought on or influences the project’s experimental design.

Background will cover the paper and context that has brought on the need for the

apparatus, existing experimental rigs and modelling used in flapping wing

experimentation, existing mechatronic applications the research could be used for, and

lastly outlining the future experimentation planned for the rig. The chapter will end with a

summary of what was learned from the chapter.

### 2.1 Project Inspiration

### 2.1.1. Key literature:

The research’s key inspiration is ‘honeybees use their wings for water surface

locomotion’ by Chris Roh et al. which is centred around analysing the honeybee’s

motion. [1] This includes proving that the method observed is using hydrofoiling as the

source of thrust and is therefore different to other forms of bio-locomotion methods found

in insects (like rowing). The report manages this by analysing a honeybee on the water’s

surface and using Particle Image Velocimetry (PIV) to measure the momentum imparted

by the wings to the water. Figure 2.1 shows an example PIV setup using a laser and

camera to study the affect of flow over a wing section. PIV studies how the particles in

the fluid are moving which can then be analysed to obtain useful data.

Figure 2.1: Example PIV experimentation [2]

The results of testing showed that the momentum created was comparable in magnitude

to the ~20µN required to overcome hydrodynamic drag [1]. This data is found by

studying the live bee’s motion; however, we will aim to use a robotic mechanism to model the motion of the wing and scale the results after. Working with a mechanism

instead of live bees avoids ethics problems and creates controllable repeatable results.

Investigating other locomotion methods like rowing shows distinct differences that are

outlined by the paper and with winged UAAV designs already out there, the hydrofoiling

motion is a far newer and more appealing motion to implement. With wings already

featured in many designs, allowing both flight and water locomotion, rowing is made

redundant as the need for fixed legs on the surface is made obsolete.


Figure 2.2: Pronate and supinate motion of honeybee wings [1]

Figure 2.2 displays the pronating and supinating that defines the honeybee’s hydrofoiling

motion. The stroke amplitude whilst the bee rests on the water surface is different to that

displayed in air, in air it is shown to have a stroke amplitude of approximately 90° [3]

whereas the study shows less than 10° on water. It also labels the angles of attack which

can then be measured and graphed through the progression of the motion as shown in

figure 2.3.

Figure 2.3: Angle of attack, α, vs. time [1]

This helps us define a range of angle of attack, α that the experimental rig should be

capable of. Although the motion falls below 20 degrees at its peak, it is worth being

capable of a wider range to allow for further analyses and optimisation to find the angles

of attack that maximise power and lift coefficients. It is also stated in the report that if the wing could detach from the water surface during the power stroke, the recovery stroke

could avoid implementing adverse thrust. [1] This means that the rig could not only

replicate the biological motion of the bee, but test for more efficient forms.

### 2.1.2. Water surface locomotion:

The paper also compares other water surface locomotion techniques like rowing. Rowing

uses hydrophobic legs to sweep or step and propel the insect or drone forward along the

water. The distinction is made that the power strokes of water walking and honeybees

differ as they occur striking down on the water and lifting the water surface respectively.

[1] There is also mention of insects using alternate biolocomotion like chemically driven

propulsion. [1] The method of rowing (or galloping) and walking are methods that can be

found in a variety of spiders that also recalls the utilisation of hydrophobic limbs to not

break the water’s surface tension and stay fixed upon the air-water boundary. [4]

The paper finally mentions the future application the study has for robotics. The potential

for an aerial-aquatic hybrid vehicle to use this motion as a its thrust source in both air

and on the surface of a body of water can be explored with future research and design

development following further modelling to maximise thrust outputs.

### 2.2. Previous Apparatus and Modelling Methods:

### 2.2.1 Existing Experimental Rigs

In the paper, to recreate the wing kinematics, a flexible wing with span of 6.4mm chord

and 19.2mm span was made with an aspect ratio (AR) of 3, and by combining this with a

function generator to power and control the wing, the motion could be replicated.


Figure 2.4: Flapping wing experimental set-up [5]

Zhao et al. features the use of an existing experimental set-up (shown in figure 2.4) to

model the flapping of wings. The design featured a bevel gear wrist that was used to

actuate the wing angle and displayed the limitation of ±45° for the stroke angle due to the geometry of the gearbox. [6] This design however utilises more degrees of freedom then

we are aiming to test for. The apparatus we aim to design will only model the stroke and

pitching of the bee’s wing whereas this model has an additional flapping motion that

complicates the design and introduces this limitation. The design varied α from -9 to 90°

in 4.5° increments, this corresponds to a total of 23 different controllable positions

through the motion. [7] The experimental rig that we aim to design should aim to model

its range of motion in a greater number of steps to allow for closer analysis of α and the

forces involved in each wing position. This papers main focus was on the flexibility of the

wing and the effect on flapping wings. With the possibility of future flexible wing research,

it would be beneficial for the apparatus we design to be capable of changing out its

testing wing. Using separate adapter designs to fix the type of wing to the chosen force

and torque sensor is the easiest way to provide this.

Figure 2.5: Flapping wing apparatus used to model stroke and pitch motion [6]

Figure 2.5 illustrates another existing apparatus that uses a pulley belt transmission

system to control the pitch and a rotating main shaft to deliver a stroke motion. This

combination is the most basic solution to delivering these two positional outputs and

should be heavily considered for implementation into our apparatus. Although this rig

was submerged for its use, the implementation of pulleys going through the water

surface could not only disturb the water but also possibly lead to slipping or lack of

effective power transmission. The design uses an ATI Nano17 force-torque sensor to

measure and record their results from their experimentation and this is a design

component that should also be considered for use. [6]


Figure 2.6: Dimensions of rectangular plate used to model the wing in hover [6]

Figure 2.6 outlines how the axis of pitching lies a quarter of the chord length, c, away

from the leading edge, and further outlines R0 as the distance from the base of the wing

to the axis of the stroke motion. R0 will vary with the apparatus’ design, however, the

distance c/4 is independent to the rig design and could be used in our modelling.

Appendix A shows some of the changes experienced in robotic flapping hovering flight

with the pitch axis at a quarter chord position and a half chord position, from these

results it is likely we will also decide to use this c/4 distance. [7]

Table 2.1: Wing parameters of three flying insects and the scaled model submerged in water with ν20◦C = 1.00 × 10−6 m² s −1 [6]

Table 2.1 provides us with a wing chord, c and span, R, that could be used in our first

round of experimentation. Although, our apparatus will allow for the substitution of wing

design, starting with a wing chord of 34mm and span of 107mm allows for the results of

this study to be replicated and compared if required, however variations may arise from

differences in the rig design and how this interacts with the fluid environment.

Finally, from this paper we can recall the equations for the coefficients of lift, drag and

power that will be calculated using our results. These are listed in Eq(1) below.

Equation 1: Equations to calculate coefficient of lift, drag and power.

Using these equations, it is possible to study the motion’s efficiency, which quantifies the

lift-to-effort ratio. Using a compilation of computer software, the apparatus’ collected

results can be optimized in the future to maximize these coefficients and improve the

motion’s effectiveness. Another study by the same authors utilises a different mechanism

design to model flapping wings, this time using a bevel gear pair to control the pitching

motion and a pulley system to drive the stroke.


Figure 2.7: Experimental set-up using to bevel gears [8]

Figure 2.7 shows the use of an outer shaft coupled to a ‘mechanism block’ that holds the

wing’s axle that provides the pitching motion. The bevel gears suggest that the design

uses an inner and outer shaft that will be driven independently, one controlling the stroke

and one the pitch. The inner shaft passes the full length of the tube and fixes to a bevel

gear that is used in a pair to then rotate the wing axle and control the wing’s α. With

components expected to be partially or fully submerged, the bevel gears design appears

far more appealing compared to the pulley, as there would be no chances of slipping or

reduction in torque. These designs are also, far more suitable than that shown in Zhao et

al. as they do not have such limitation in stroke amplitude, allowing for a minimum 180°

(compared to 90°), being restrained only by the sensor wire.

### 2.2.2. Wing Modelling:

To achieve results that can be considered comparable we need to prove that correct

modelling methods are being chosen. Investigating the available methods of analysing

wing responses show that using a straight leading edge on the wings ‘are desirable for

increased performance’ [8], this alongside with the existing apparatus analysed in

Section 2.2.1 allows us to confidently chose a rectangular wing form. With existing plans

to ensure the apparatus can substitute its chosen test wing, we will be able to confidently

test a wide range of AR and also explore flexible wings. This gives the maximum

opportunity for finding a wing shape that will produce the most thrust from the motion.

A variety of wing shapes and sizes could be used in our modelling but for the purpose of

our initial testing, a specific wing must be chosen. It has already been seen from

previous rigs that a rectangular wing, chord length of 34mm and span of 107mm is most

likely to be used however this choice must be justified. Many studies into oscillating and

flapping wings vary in their chosen AR. AR is defined as c/R and is a method of

attributing the shape of the wing. One study based on flexible wings for Micro Air

Vehicles (MAVs), used a range of 1 to 6 for their AR [10] whereas another study for

underwater vehicles (UVs) used a range of 3 to 10. [11] Finally, a paper investigating the

use of flexible flapping wings for Unmanned Aerial Vehicles (UAVs) used a wing of AR of

4 with 60mm chord length and 240mm span. [12] Although these three all serve for

different applications; they reinforce the initially chosen AR of 3.15 and show strong

support for this choice.

Future modelling and UAAV design may decide to use multiple oscillating hydrofoils,

research into this has shown that there is little enhancement after a series of three,

however this may change with modelling in different motions and with different hydrofoil

spacings. [13]

### 2.3. UAAVs and MAVs

### 2.3.1. Existing UAAV designs and application potential:

UAAVs are a useful developing technology that has a strong variety of applications,

including imaging, surveying, communication [14], checking oil spills [15], sample data

collection like algae [16], and general water quality monitoring.[17] The bright advantage

of the UAAVs is that they can find the samples, like an oil spill or a collection of algae

from the air, land directly nearby and start sampling data, creating a more efficient

method than currently used. They are most commonly powered by jet-thrust, propellers

or flapping wings. [18]

The common issue with UAAVs is the struggle to leave the air-water boundary after

landing, this is further complicated by vehicles that travel under the water’s surface. To

allow some designs to perform underwater, they require subsystems that drain and flood

compartments when needed. [19]. In fixed wing designs this is because as the chord

length increases for a set aerofoil section, the buoyancy force per unit span increases

quadratically, making it challenging for the drone to stay submerged. [20] Another

solution used is sets of propellers that output forces strong enough to not only drive the drone through the water but also keep it submerged at the same time. [21] Hybrid

Underwater-Aerial Vehicles (HUAVs) exist that incorporate both these features to

overcome this issue. [22] There is wide variety of UAAV designs already being explored

as shown below in table 2.2.

Table 2.2: Existing UAAV designs [23]

Table 2.2 shows the propulsion methods for the designs and with many of them using

fixed-wings for aerial flight it leaves potential to mobilise the wings to implement the

honeybee’s motion and navigate the water surface with an alternate propulsion method.

### 2.3.2. MAVs potential:

Flapping wing research on insects is a consistently explored area and from this, robotic

insect MAVs have been designed. [24] The advantage of MAV’s is that they could be

deployed in large numbers for search and sampling applications, however they hold no

capability for payload or cargo. [25] MAVs are defined as being no greater than 15-20cm

long [26] (for example the Delfly micro uses a 10cm wingspan [27]) and whilst we plan on

modelling a greater wing, the results could be scaled to the smaller application. It is also

reiterated the importance of not just copying the biological solutions for these drones but

also then improving the motion to get the maximum efficiency from them. [27]

### 2.4. Future experimentation environment and methodology:

Future experimentation will occur at a University of Southampton (UOS) laboratory and

first involve using the apparatus in a static water tank. The available tank is of

measurements 1x1x2m and will be partially filled to a suitable length/depth depending on

the apparatus design. The testing involves a lower torque requirement to run the

apparatus through the water (in comparison to flowing water). A brief overview of the

methodology involves first fixing the rig above the tank and then programming motors to

create the desired motion and finally running the program whilst saving data from the

force-torque sensor at a sampling frequency of 1000Hz [7]. The programmed motion can

then be compared to the results over time to attribute results to α and stroke position.

This applies to the second round of testing in a recirculating water tunnel (RWT) with the difference being the addition of the water flowing at a set speed. The available RWT has

an experimental test section measured 1.2x0.8x0.8m and allows a maximum flow speed

of 1m/s. This 1m/s test limit allows us to design for the required torque to drive the

apparatus in this environment and overcome the drag forces involved in the motion,

however, in reality, the testing will initially be done at 0.3m/s and this is the speed we

should design for. The forces will however depend on the wing area for the pitch motion

and the apparatus area for the stroke motion.

The two experiments will allow for the finding of coefficients at individual points

throughout the motion as mentioned in the previous literature. This will then allow for

experimentation and optimization to get greater thrust and power from the motion. This

then will allow for implementation into UAAV designs and future application. The Lab

equipment used to test the apparatus will have no limitation for design height and

requires only the correct frame to fix the apparatus to. This can be done using an

arrangement of metal extrusion lengths fixed together that can be bolted to. The UOS lab

equipment has an existing extrusion frame above the tanks and they will be the chosen

point of mounting.

### 2.5. Background Summary:

The background research that has been covered will be what influences the final

apparatus design criterion. From the research we learned a suitable modelling wing size

to take forward and also the existing systems being used to create the motion. We can

investigate the use of bevel gears and pulley systems as they are the most appealing

and secure method of power transfer. Other gearing systems are available but are

unlikely to be our first choice. The honeybee’s motion, along with other insect’s and bird’s

wing flapping, has been shown to be modellable using a harmonic sinusoidal function

like a cosine wave. This could be coded into a software like MATLAB and inputted into a

set of stepper motors. This also means that alongside two stepper motors, I will need two

signal converters to process the cosine functions and allow the motors to output the

motion. The range of the honeybee’s wing positions can be broadly covered with a ±45°

α and 90-180° stroke length and so this is the target capability for the design.

The research into existing UAAVs has shown how the data that will be collected from this

apparatus will be used to developed new locomotion strategies and open up the

possibility for a new wave of designs. MAVs are also a developing technology that could

incorporate the movement on a smaller scale to benefit its design issues. UAAVs have a

wide variety of uses in the future of automation and research, therefore the potential

beneficial impact the future research could have is large.

Finally, by planning ahead the future methodology of experimentation, it was found the

lab equipment and testing implemented only minor design constraints like the overall

height of the apparatus to allow sufficient submersion into the tanks and the planned

modelling speed of the flowing water in the RWT. With this, all the required information

has been collated and is ready to be taken forward into the design process.

### 3. Developmental Design Process:

Taking inspiration from the previous experimental apparatus, initial design drawings

could be made to investigate some variations of the key design features like the

arrangement of the bevel gear assembly and the mounting of the sensor. These initial

drawings are then developed into CAD models depicting the exact scaled components

used in the final rig. Analysis into the implementation and effectiveness of key design

features are made and then a final component material is chosen. Brief validation is

made, comparing the final design to any targets made in the Section 2.

### 3.1. Initial sketches:

Using figure 2.7 as the initial inspiration, sketches were made to investigate possible

design solutions to the complicated assembly required to achieve such a design. This

included the ability to provide torque down to the bevel gears without the issue of

backlash.


Figure 3.1: Initial design sketch of bevel gear sub-assembly

Figure 3.2: Detailed developed design sketch

Figure 3.3: Sensor mounting strategy

Figures 3.1, .3.2 and 3.3 show the initial designs surrounding the mounting of the sensor,

bevel gears and shaft inputs.


Figure 3.4: Initial sketch fixing stepper motor to board

Figure 3.5: Initial sketch fixing stepper motor to outer shaft

Figures 3.4 and 3.5 show the possible solutions to the backlash issue where the stroke

motion causes a change in pitch angle as one bevel gear rotates around another. Either

the stepper motor is fixed to the board and programmed to rotate in sync with the stroke

motion, or the stepper motor is mounted to the outer shaft as to rotate in unison.

Figure 3.6: Target wing and stroke angle range

Figure 3.6 illustrates the range of positions we are aiming to achieve with the design with

reference to a neutral position at an angle of 0°.

### 3.2. Design Fundamentals:

### 3.2.1 Design Overview:

The initial CAD designs of the two basic sub-assemblies are shown below. Figure 3.7

shows the motor and pulley systems that provide the mechanical input, whilst figure 3.8

shows the bevel gear system that transfers motion through to the wing.


Figure 3.7: Motor and pulley system sub-assembly

Figure 3.8: Bevel gear system sub-assembly

Both stepper motors have their outputs processed through a form of gearing that

changes the speed, torque and output step resolution size. These provide great design

flexibility to aid in providing sufficient torque or more desirable resolution sizing. The

pulley system can convert the motor output into rotation of the outer shaft therefore

changing the stroke angle. The second stepper motor instead uses an inner shaft and bevel gears to actuate a change in wing pitch angle by changing the axis of rotation by

90°.

To reduce the effects of deflection on the inner shaft, a pair of deep groove ball bearings

are used. These can be inserted at either end of the outer shaft ensuring alignment

between the inner and outer shafts at either ends. The positioning of these bearings in

the shaft are displayed in the sectional view in figure 3.9 and use a changing in shaft

thickness as a shoulder to hold the bearings in position.

Figure 3.9: Assembly of Outer shaft, Inner shaft and alignment bearings

The length of the outer shaft was chosen at 0.6m which allows for ~0.5m of reach into

the water tank. This allows the motors and signal converters to be mounted at distance

from the water and create no risk of damage. This also aids in the mounting to the

existing frames that are positioned above the tanks.

The initial design can then be developed further by creating a suitable mounting

arrangement. This includes adding the main 12mm plywood mounting board

accompanied with a flanged bearing. The flanged bearing is crucial to the design, as it is

the most effective way to fix the outer shaft at a certain height whilst still permitting

rotation. The board includes a series of slotted cut-outs to permit the fixing of the board

to a mounting frame and also the pulley stepper motor onto the board. Figure 3.10 shows

the produced board with attached bearing and motor.


Figure 3.10: Image of manufactured mounting board

Implementing this completes the overall design and allows the creation of a final CAD

overview. This finalised design can be seen in figure 3.11.

Figure 3.11: Final Apparatus design

The image also includes an aluminium extrusion frame that will then be fixed to the lab

tank’s frame. These lengths of extruded aluminium are linked together using right-angled

brackets depicted above as triangular components. A visualisation of the apparatus

positioned above the UOS static water tank is shown in figure 3.12.

Figure 3.12: Flapping wing apparatus positioned on the water tank frame.

### 3.2.2. Power Transmission:

To explore how we can provide the required torque, we have to think about the two

required features of the motion separately. To achieve the motion, we will start by

needing to choose a motor, and after consideration outlined in Section 3.5.1 the chosen

motor is the STM-23S-3RE which is rated with a torque of 1.41Nm [28]. If we then

compare this to the required torque to perform the pitch and stroke motion, we know that

the stroke exceeds that provided by the motor whilst the pitch falls dramatically below.

This means that a gear system is required to be able to change the supplied torque and

enable the experimentation. Using Trequired/Tmotor = Gear ratio (GR), it can be said for the stroke motion the torque is out by a factor/gear ratio of 4, whereas the pitch torque can

be supplied by the motor.

During the design process, multiple gearing systems needed to be explored including

bevel gears, spur gears and pulley systems. Comparing these methods is important to

justify which method we proceed with whilst also weighing up against costing. Using

bevel gears comes with a great increase in cost which is not justifiable for the stroke

motion when compared to the alternate methods. Whilst during the literature review, we

learned that pulley systems whilst simple can leave room for error if not properly taught.

[12]

Eliminating bevel gears for the stroke motion, Table 3.1 compares the possible methods

we could have employed to achieve the gear ratio of 4.

Table 3.1: Spur gear vs. Toothed timing belt pulley

The chosen method of power transmission is the use of a high torque drive (HTD) timing

belt and pulley set. This was the most suitable of the options for our purpose and our

situation. This involves the factors of accuracy, manufacturing, assembly and budget.

The pulley system comes in 4 components: a 48-tooth driven pulley, a 12-tooth driving

pulley, a 425mm-long HTD belt and a locking bush (all shown in figure 3.13). The

number of teeth on the pulleys decide the gear ratio, and therefore 48/12 = GR = 4.

Figure 3.13: Purchased HTD toothed pulley components

The sizing of these components can be used to diagrammatically show the mounting

distance between pulley centres in figure 3.14. This distance effects the design of the

mounting board and where the stepper motor would be positioned.


Figure 3.14: Diagram of pulley spacing, diameters and belt length

For the pitch motion there is no need to increase the torque, this does not mean the gear

ratio will be irrelevant, there is instead value in trying to increase the resolution of the

wing position. With the motor having a 1.8° resolution [28] and the target wing position

range of ±45°, a finer degree in wing position is required. It was decided, the design will

use a set of bevel gears to change the axis of rotation from the y-axis to the x-axis so by

choosing an applicable gear ratio we can increase the accuracy of the resolution.

A set of steel bevel gears were found with a 1.5 GR, using a 16-tooth driving gear and

24-tooth driven gear (pictured in figure 3.15 below). This 1.5 GR then creates a 1.2° pitch

angle resolution for the rig, which can be further improved with an planetary gearbox.

The gears are ordered with set screws, and a 10mm (16-tooth) and 21mm (24-tooth)

bore corresponding the design of the inner shaft and wing axle.


Figure 3.15: a) Steel bevel gear pair in Solidworks (top), Purchased bevel gears (bottom)

Using the gear manufacturer’s provided mounting distances (base of one gear to centre

of second gear) of 40mm and 37mm [29], it was possible to ensure these distances were

properly implemented like shown below in figure 3.16.

Figure 3.16: Mounting distances for the bevel gears

### 3.2.3. Wing, Sensor and Adapter:

The chosen wing model was the same as that found in the literature and that is a

rectangular plate of chord 34mm and span of 107mm. The ATI Nano17 IP68 is a sensor

model submergible in fresh water to a depth of 10 meters and has a force and torque

resolution of 3.13mN and 0.0156Nmm respectively. [30] The sensor is available for me to

use from the UOS and uses an arrangement of threaded holes for both mounting of the

wing and to the apparatus. To therefore to fix the acrylic plate to the sensor, an adapter

will need to be designed that fixes the two together.


Figure 3.17: a) CAD of wing and adapter assembly (top), b) Manufactured adapter with

acrylic wing (bottom)

Figure 3.17a) shows the design that will be implemented. Figure 3.17b) shows the

manufactured adapter and how it holds the plate on either side with two prongs in a

pressure fit that can be glued to create full security. The design of the prongs mean that

they only protrude into the wing only 10mm and have a thickness of ~2mm as to not

dramatically affect the flow over the wings and be a factor in the experimentation’s

results. Example flow over the wing can be modelled using software like Solidworks Flow

Simulation, figure 3.18 shows an example flow path.


Figure 3.18: Flow visualisation over the wing

The problem the Nano17 sensor poses to the apparatus is the route the axially-exiting

cable must take. A path must exist for the sensors wire to pass through otherwise the

design will not work. To allow for this, the components have been designed to either

allow for the sensor to pass through them with the cable following or use a cut channel

for example the wing axle and the back plate that mounts the sensor. The back of the

sensor and the wire can be seen from the rear of the apparatus as shown in figure 3.19.

Figure 3.19: Nano17 sensor wiring route

### 3.2.4. Motion Mechanisms:

Both mechanisms are powered by the chosen stepper motor and controlled with a signal

converter. The waveforms will be coded on a software like MATLAB and then uploaded

to the motors causing the actuation. The software allows for a wide flexibility of waveforms and programmable motions being able to control the motions amplitudes and

frequencies.

### 3.2.4.1. Pitch Mechanism:

In the case of the pitch motion, the outputted motion will pass through an planetary

gearbox reducing the resolution with a GR of 1:6 down to just 0.3°. This then travels the

length of the inner shaft where it drives the bevel gear pair reducing the resolution value

once more down to a final 0.2°. The overall GR from input to output is 1:9 and therefore

to create the 90° change in α from -45° to +45°, the stepper motor needs to complete

810° of rotation (or 2.25 revolutions).

To continue the output from the 12mm gearbox shaft [31] to the 10mm inner shaft, a

Ruland Jaw coupler is used. Shown in figure 3.20, the coupler is made of 3 pieces: two

jaws and one rubber spacer. Each component is ordered separately and therefore

compatibility must be checked.


Figure 3.20: Ruland jaw coupling [32]

A 12mm bore and 10mm bore set of jaws were selected with the corresponding 33mm

diameter rubber coupling between. The jaws fix to the shafts by tightening the screw in

the side of the jaw. This form of coupler has been chosen as it further helps the

alignment of power output and flexes to ensure this. If the coupler experiences axial

loading however, it will separate apart. To stop this, it is possible to further machine the

coupler and use a fixing to hold the two jaws together.

Figure 3.21 shows 3 positions of the wing, these are 0, -45° and +45°. These angles

correspond to the neutral position, and maximum and minimum angles of attacks.

Figure 3.21: Apparatus at pitch angles: 0, -45° and +45°

These angles are shown clearer using a 2D drawing from the view of the wing tip in

figure 3.22.

Figure 3.22: 2D drawing of pitch motion

### 3.2.4.2. Stroke Mechanism:

In the case of the stroke motion, the motor first rotates the small 12-toothed pulley, this

then uses the timing belt to rotate the larger pulley and therefore also the outer shaft.

The pulley gear ratio of 4 means that a total 5.64Nm torque acts on the outer shaft. This

also means the stroke positions has a 0.45° positional resolution.

Figure 3.23 shows the full 90° sweeping range that will be employed in testing. The

apparatus is capable of a sweep greater than 90° however this would start to cause

issues with the sensor wire wrapping and stretching as it covers such a large motion.


Figure 3.23: Apparatus at stroke positions: 0, 45° and 90°

These angles are once again shown clearer using a 2D drawing this time from above in

figure 3.24.


Figure 3.24: 2D drawing of stroke motion

### 3.3. Material Selection:

The choosing of materials involves a careful balance of mechanical properties and

budgeting/availability. The ideal material for the set-up will have substantial strength

compared to its weight. To allow for ease of assembly and lower resistive weights/forces,

a reduced weight is optimal. The only components that are affected by serious loads are

the inner and outer shafts. These are the components where strength will be required. If

the material is not strong enough, the component will deform and fail. The property that

will gives a good indication of failure is the material’s yield strength.

Shown below in figure 3.25 is a comparison produced using GRANTA Edupack to create

a comparison between yield strengths for a range of materials. The materials have been

limited to predominantly plastics and metals that wont rust. This is because of the water

environment of the testing.

Figure 3.25: Yield strength against density for potential materials

Engineering design projects depend on a variety of inputs and one of the strong

limitations is the project budgeting. After assessing the possible materials, only stainless

steel and aluminium are reasonable choices. Both these materials are sufficiently strong

enough and suitable for water-submersion without serious corroding which is the main

priority for testing. Between aluminium and stainless steel, the main difference is their strengths. Stainless steel not only has a greater density (7900Kg/m³ compared to

2700Kg/m³
[33,34]) but also a greater Young’s Modulus than aluminium (190GPa

compared to 70GPa [33,34]), which means that it would be less impacted by the effects

of vibration. However, due to these material properties, the apparatus would be heavier

and the time and material costs are far greater. This means for our production we will

have to use aluminium for the construction. This material is far softer and allows for

quicker additional machining were tolerances not great enough and extra machining was

required. 6082 T6 Aluminium is readily available inside the Engineering Design and

Manufacturing Centre (EDMC) and is kept in constant stock.

The bevel gears are manufactured from EN8 mild steel, and therefore will require begin

to rust over time from being submerged in water. This means the gears will require

drying after use to slow down this process and eventually may need treatment or

replacing. The material used for the wing plate is clear acrylic laser cut in the EDMC

whilst the 3D printed adapter is produced from Polylactic acid (PLA). These are both

cheap and easily accessible from the University.

### 3.4. Design Validation:

### 3.4.1. Design Capabilities and Customisation:

The design would theoretically allow for unimpeded rotation for a full 360° for both axis of

movements however this is limited by the sensor’s data/power cable. This cable could

pose the problem of not only twisting the cable but also tangling or pulling out of its

power pack if it was to be stretched too far. The cable could theoretically be clipped onto

the outer shaft to stop such free motion in the water however this would not completely

solve the issue especially the cable twisting. Because of this the angle of attack should

not be used past ±90°, whilst the stroke motion should only be used to a maximum 180°

sweep.

The design has been made in a way that allows for simple customisation and changes

that allows for a variety of future experimentation and improvements.


Figure 3.26: Apparatus section above the tank

The final mounting apparatus shown in figure 3.26 uses simple connections and a

modular design to separate the fixings attributed to each component. In the future a

different stepper motor with higher torque or finer resolution may want to be used, and as

the motor and the gearbox is fixed to a customised plate, a new plate could be designed

and swapped in to implement this change without effecting the rest of the set-up. As for

the pulley system motor, redesigning and creating a new plywood board would be simple

and cheap to create.

If the apparatus was to be used in flow greater than planned for, the required torque

through the pulley would be greater. If this was to be the case, a new pulley could be

ordered, compatible with the current locking bush, but with a greater number of teeth.

This would increase the GR and possibly solve this issue. This is only applicable up until

the maximum pulley size compatible with the bush.

Figure 3.27: 3D printed adapter from wing to sensor

The PLA adapter pictured in figure 3.27 couples the sensor to the rectangular plate wing

we chose at the start of this project. There is a lot of possible research with different wing

shapes, their aspect ratio but also the effect of the wing flexibility. When this round of

research is required, another adapter can be quickly 3D printed and attached onto the

sensor. All the adapter needs are three M2 clearance holes corresponding to the sensors

interface. The pronged design should be capable of holding a wide variety of AR as long

as the lengths do not become too great. If the plate thickness was also to be changed,

the spacing between the prongs would also require changing. However, for a flexible

wing an alternative to the prongs would need to be designed, likely involving two rods the

flexible material would be secured on.

### 3.4.2. Torque Requirements:

Now that the core of the set-up is designed, the expected torque of using the rig in the

RWT can be calculated. As mentioned earlier, this will allow us to choose what driving

torque we need to provide for the rig to function. The area used for modelling the

resistive forces has been found from our current design. For the stroke motion, the side-

on area of the sub-assembly is related to the force experienced in flow as shown in the

equation written below.

F =
2

CDρAUinf

Equation 2: Force exerted by flowing fluid

Uinf = Vinf + 2πfR

Equation 3: Equivalent flow speed for object oscillating in fluid flow

First using Eq(3) an equivalent flow speed can be found to be used to calculate the

torque. Modelling in the recirculating water tank will be done at Vinf 0.3m/s and at an

apparatus frequency of 1Hz. By combining this with the largest distances to the axes of

rotation, Rstroke = 140mm (0.14m) and Rpitch = 25.5mm (0.0255m), a calculation can be

done to find Uinf. These calculations are shown below:

Uinf,stroke = 0.3 + 2π × 1 × 0.14 = 1.18m/s

Uinf,pitcℎ = 0.3 + 2π × 1 × 0.0255 = 0.46m/s

Using CD = ~2 [35], these values can be used for the force calculation outlined in Eq(2). These calculations are shown below (with ρ = 1000kg/m³
):

Fstroke =

1
2

× 2 × 1000 × (0.241 × 0.9) × 1.18² = 30.2N

Fpitcℎ =

1
2

× 2 × 1000 × (0.034 × 0.107) × 0.46² = 0.770N

Then by using T = F*R, the maximum torque can finally be found. This yields the results

Tstroke = 4.228Nm and Tpitch = 0.196Nm. The torque involved in the pitch motion is minimal

and even if this underestimates the required torque, a stepper motor is likely to be able to

drive it. The stroke torque overestimates the area involved in the motion greatly, it should

then follow that if this torque can be provided, the apparatus will be capable of full

function.

### 3.4.3. Design Resolution:

The resolution of the design has been decided by the motors, gearbox and gears. The

final resolution of the wing angle of attack is 0.2° whilst the stroke position resolution is

0.45°.

Figure 3.28: Image of planetary gearbox

The motors each have 1.8° resolution and then after a 1:6 gearbox (example shown in

figure 3.28) and 1:1.5 bevel gear pair give the 0.2° whilst the 1:4 pulley gear ratio gives

the 0.45°. These resolutions are sufficient for our experimentation and allows for fine

control over the wing position over time. However, this could be further improved with a

change of components if ever required. By changing out the motors or gearbox the

resolution could changed until satisfactory, however this requires the purchasing of

components far beyond our budget. The motor we used has a Nema23 shape type and

specific shaft size, if the available gearbox was not compatible with this shape, then

either one would require purchasing or the design would need to proceed without a

gearbox and a much poorer resolution of 1.2°. Therefore, it was fortunate there was a

compatible gearbox readily available to be used. The motors mount flush to the flange

ending of the gearbox using four M5 screws and nuts. The arrangement of these

components can be seen in figure 3.29.


Figure 3.29: Nema23 stepper motor shape mounted to compatible gearbox

In addition to the positioning resolution, as stated earlier in Section 3.2.3, the sensor also

has a force and torque measuring resolution of 3.13mN and 0.0156Nmm respectively.

They are the fine degrees that our results will be accurate to and so this is very important

to be aware of. If our resolution was not sufficiently small enough, the data gained would

be useless as there would be far less detail and variation.

### 3.4.4. FEA Analysis:

The functionality of the project has been thoroughly validated and rationalised, however

no assessment has been made for structural stability. A simplified Finite Element

Analysis (FEA) model of the outer shaft would show the forces experienced during

testing. The analysis would involve assigning appropriate constraints (like the flange

bearing only permitting rotational motion and no axial deflection) and modelling the

4.228Nm torque experienced by the stroke motion.

Figure 3.30: Example FEA mesh on a cylindrical shaft [36]

Figure 3.30 shows an example mesh on the cylindrical shaft, the number of elements will

affect both the model accuracy and processing time. The model can have an appropriate

mesh sizing applied and solved for shear forces throughout the length. The results of this

modelling can be compared to the materials yield strength to prove if the material would

shear or not and what safety factor is in effect for the rig. Further modelling to show shaft

deflection could also be performed as this could affect the accuracy of the modelling

motion position.

### 3.5. Motor Control and Data Recording:

### 3.5.1. Motor Selection

To deliver the motion we have designed for, two motors need to be used, each

controlling their own axis of the motion. For our experimentation, the prioritised aspects

for the motors, are the torque, step size (resolution) and costing. Servo and stepper motors are the two most common types, both are suitable for application and therefore a

choice needs to be made on which to employ. Whilst servomotors typically are more

efficient and capable of a greater torque, stepper motors tend to have a stronger holding

torque. The holding torque is an important factor as the motor actuating the pitching

motion will use this to ensure the inner shaft rotates in sync with the outer. Stepper

motors are capable of producing the required torque and with a great availability of

models accessible through the UOS, this was the motor type that was chosen.

The STM-23S-3RE stepper motor was chosen due to availability within the university.

Appendix B displays the engineering drawings for this motor, with key information like the

mounting information and output shaft dimensions clearly defined. Table 3.2 lists some of

the key technical values related to the motor including the power requirements that will

need to be supplied.


Table 3.2: Stepper motor technical data

### 3.5.2. Software Programming

The chosen motor will be programmed by inputting serial commands written into a

software like MATLAB. To allow the motor to interpret the information coming from the

software it must be translated using a USB-to-Serial Converter. Imaged below in Figure

3.31, is the ES-U-3001-M model that will be used.

Figure 3.31: ES-U-3001-M USB-to-Serial data converter [37]

Experimentation will require two units (one for each motor), the converter uses a simple

cable (similar to that used on Arduino R3 boards) to receive data from a computer whilst

6 pins are used to transfer the data to the stepper motor. Out of these 6 pins, only 5 will

be used, and will uses lengths of male-to-female wires to connect to the motors. Table

3.3 lists the connections from the converter to the motor.


Table 3.3: Converter to Motor wire connections

### 3.5.3. Sensor Data Reading

As mentioned earlier in Section 3.2.3, the sensor we had chosen to use is the ATI

Nano17 IP68 model. The model is fitted with an axial cable shown in appendix C that

exits the rear of the sensor and is plugged into an Interface Power Supply (IFPS) box.

This box will connect into its power supply (can be wall mounted supplies depending on

the model) and also use a 26-pin female DAQ port to allow for data collection. An

example IFPS is shown in figure 3.31 with labelled DAQ port.

Figure 3.32: IFPS Box [38]

The sensor produces transducer data that is then interpretated by a DAQ device. The

device converts the incoming data into force and torque readings experienced by the

sensor. These values can then be either saved to a data card or transferred via USB

straight to a computer. Post-processing and analysis of these results can be performed

computationally after that.

### 4. Manufacturing:

This section will outline any manufacturing steps and changes that were made compared

to the theoretical final design. The engineering drawings for the final design components

manufactured in the EDMC are shown in Appendix D. For this project we were provided

with financial budget of £100 and an additional budget of 21 hours of EDMC technician

time. Any problems and changes made to adhere to this budget have been stated in the

following sub-section.

### 4.1 Budgeting changes

Now the final design is in hand it is important to draft up a costing for each component in

the design. This has been done and is shown in table 4.1 and 4.2.


Table 4.1: Costing of Manufactured components

Table 4.2: Costing of purchased components

Some of the components are stated to read £0 and free of charge. This is due the

component being available for use from previous projects or are just not produced from

materials the University charges for. For the EDMC to produce the rig’s components

completely from stainless steel would have required 32.5 hours of technician time. This is

why aluminium was chosen to produce the apparatus. However even from aluminium,

the manufacturing time would still have been too great. To work around this, I would be

required to perform my own additional machining. This is far easier working with the

softer aluminium and so this is a suitable solution to the problem. The components the

EDMC produce will use hole sizes suitable for additional tapping post-production. I can

then tap the threads into these holes and also implement a countersink when necessary.

Simple components like the inner shaft and standoffs were removed from EDMC

processing. This is because I could purchase existing female-to-female threaded 60mm

standoffs (shown in figure 4.1) instead and I could cut the 10mm diameter bar (inner

shaft) to length myself.

Figure 4.1: Four M6 60mm long hexagonal Standoffs


Figure 4.2: a) initial proposed design (top), b) manufactured design (bottom)

Despite this, the machining hours would still remain too great if the design was not

changed. The desired design could not be produced and to meet budget restrictions, the

mechanism block was produced to a far less streamline and lightweight design. Shown in

contrast between figure 4.2 a) and b), it is seen that the cut along the back of the

mechanism block and the 20mm fillet on the bottom have been removed to meet budget

and fall to 20 hours of technician time. The milling of this component used too many

EDMC and there was no other choice but to make this call. Fortunately, the second

curved fillet on the block was not needed to be removed, this would be severely

problematic as it is a fixing point for assembly and must not be removed.

Unfortunately, this could impact the experimental results as this will create greater

disturbance to any water flow, however fortunately it will not stop the apparatus from

functioning. Due to the overestimation in area of the required torque, the manufactured

design is still capable of full motion and will be fully operational.

The last manufacturing change I had to implement is the addition of a set screw to the

smaller pulley, depicted in figure 4.3 below.


Figure 4.3: Image of driving pulley [39]

The pulley comes with a pilot bore, this can then be machined out to 6.35mm. However,

relying on a friction fit is not suitable for power transmission and therefore instead it

requires the addition of a set screw which permits for up to a more general 6.5mm bore

and guaranteed transmission. The issue with this is where to add the set screw, there is

two options in locations. The set screw can be drilled into the tooth area of the pulley, but

this may compromise drive effectiveness, or it could be located in a small area of excess

material at the neck of the pulley. This area is 5.5mm wide and just allows for an M! or

M2 set screw to be fitted. This should be sufficient to pin to the flat face of the stepper

motor drive shaft.

### 4.2. Outer shaft

The outer shaft required specific machining for the design to work. Due to availability the

only sizes of bearings that could accompany the 10mm inner shaft were 26mm OD. The

outer shaft has an inner diameter (ID) of 26mm and therefore at either end the shaft

required an 8mm deep thickness reduction from 3mm to 2mm. This can be shown with a

detailed and section view onto the outer shaft. This view is shown in Figure 4.4.

Figure 4.4: Section view of bearing arrangement

### 4.3. Overall Mechanism assembly

The steps required for successful assembly have been briefly outlined in Appendix E.

These steps ensure the sensor is successfully installed, the gears interact properly and

the set-up is mounted securely. The order of assembly is very important to have due to

the components only fitting together in a certain order and sometimes requires

performing multiple steps simultaneously. Creating a design that assembled was one of

the most complex problems to overcome through this project, as the sizing of

components had to be carefully thought out to allow clearance space but also fairly tight

fittings to stop large levels of vibration. 1mm clearances and fitting spacing was decided

as appropriate and used repeatedly across the design.

In the final stages of manufacturing, an error had been noticed with the sensor that was

design for. The IP68 variation of the Nano17 does not have a 17mm diameter like the

other models. Instead, a large 20.1mm diameter is used. To allow for assembly and

allow the sensor to pass through the bores of other components, components had to be

taken to the EDMC and rebored to a large 21mm instead of the original 20.1mm that was

used. In addition, a new back plate was design and manufactured in the EDMC that was

compatible with the mounting interface of the correct sensor.

### 4.4. Mounting

Possibly the key component in the mounting of the rig, is the flange bearing. This bearing

allows for the design to be held in place at a pre-chosen height using a pair of two set

screws. The bearing holds the rig but also permits for the outer shaft to rotate, which is

crucial for the function of the stroke motion. Other alternatives like low-friction bushes and shoulders were investigated but not implemented. The chosen bearing is illustrated

in figure 4.5 and depicts the four interfacing bolt holes that secure it.


Figure 4.5: 4 Bolt flange bearing [40]

Following the selection of this component, a mounting board was design to allow for its

fixing.

Figure 4.6: Mounting Plywood board

From figure 4.6 it can be seen that the board has been designed with corresponding

holes for the flange bearing, slots and reduced thickness for the motor mounting and

finally, slots for the frame fixing. The frame slots are 9mm wide along the outside edges

of the board and allow for M8 bolts to fix through with washers into M8 inserts in T-slots

extrusions.


Figure 4.7: T-slot aluminium framing arrangement

Figure 4.7 shows the arrangement of framing that will allow the board to fix to. This can

then be held together and bolted to the existing framing above the tanks using right-

angled brackets (depicted as triangular components). The depicted grooves show where

the M8 threaded inserts will be added to bolt into. The final bolted mounting assembly is

shown below in figure 4.8.

Figure 4.8: Final mounting assembly

### 4.5. Electronics

Using the available Electronic Workshop facilities on campus, wiring of appropriate

length could be cut and prepared. By soldering together, the long cut lengths of wires to

shorter existing wires with the necessary female pin connectors, the connection between

motor and signal converters can be produced. For safety purposes, these solder joints

are covered in heat shrink to insulate the joints. The power wiring for the stepper motors is produced with the same methodology, however differing with connector types. The

power connector into the motor uses additional screws to fix the connection to the motor

and prevent it from pulling loose. On the other end of this wire is a connector that will

plug into the 5V laboratory power supply.

The power supplies, IFPS and DAQ are all provided by the UOS Boldrewood Campus.

This equipment is held in the laboratories and can be taken out for use at the time of

experimentation. A quick risk assessment reveals that the main issue with electronic

equipment is the proximity to water. Waterproofing the entire rig would be a long and

expensive process. Alternatively, the rig has been carefully designed and positioned so

the motors stay a safe distance from the water surface. The experimentation does not

involve great speeds or water disturbance and therefore should not be presented with

the risk of splashes, however if this turned out not to be the case, a splash guard (acrylic

sheet) could be mounted to completely eliminate this risk.

### 5. Conclusion:

The design process of this experimental set-up has been a long and methodical process,

constantly adhering to restrictions and budgeting challenges. Whilst drawing a great deal

of inspiration from an existing design, there was still a large number of design issues to

work around. Whilst this report has briefly covered the design requirements of each

component and some of the thought process behind them, it does not cover the repeated

iterative process of change that was needed to create a fully working design. Due to the

dependency of neighbouring components, there were many occasions where the design

required full remodelling due to new design inputs and decisions.

To conclude, the design of the rig has yielded an arrangement that meets its initial aims

by allowing for the measurement and calculation of torque and power coefficients that

can be used in further studies to influence the plausibility of using the hydrofoiling

method in winged UAAV systems. The final design can be summarised as an aluminium

apparatus capable of delivering rotation in two axes to create a sinusoidal waveform at

the wing tip within 0.2° and 0.45° positional accuracy. The set-up uses stepper motors

programmed with signal converters to create a sinusoidal wave form output at the wing.

This motion is then to be performed in a laboratory environment in pre-chosen

conditions, and measurements can be taken from the Nano17 sensor.

The results from this testing will allow for power, lift and drag coefficients at separate

positions along the motion to be calculated. This study then allows for further

experimentation to idealise these coefficients and make the most efficient motion with the

greatest thrust production. This is the motion that would then be implemented into the

future robotic drone designs.

### 6. Future work and Experimentation:

### 6.1. Mechanism improvements

Due to budgeting and timing constraint, there is still far more work to do to achieve useful

results and implement possible design improvements. The improvements will allow for

decreased drag and therefore less interference with the water environment and results.

As stated in section 4.1, the design was changed for manufacturing and therefore the

first improvements would revolve around reversing these design changes and

streamlining the set-up once more.

### 6.2. Motor and gearbox alternatives

Following this, the design could be changed to shed weight and increase positional

resolution. There are three ways for the design’s resolution to be made finer. Firstly, a

gearbox with a greater gear ratio can be used, however this will increase the overall

apparatus weight and height. Secondly, a different stepper motor could be used with a

lighter weight and finer step sizing. And lastly and most suitably, investigate the use of

the motor’s half-step and micro-stepping functions. The motors micro-steps allow for less

than 1.8° movement and this then means the gearbox can be removed from the design

reducing weight. The motors weigh 1.19kg each [28] and so being able to not remove the

further weight from the gearbox is an appealing possibility. The gearbox also has a

height of 71mm [31] and being able to reduce the overall height of the design further

reduces the effects of vibration. Seeing as the motor will be the source of the vibration

this is a very effective improvement. The overall height of the design stands at 920mm,

this is separated into 578mm below the plywood mounting board and 330mm above.

With the removal of the gearbox the height above the board would drop 22% and overall

length would be reduced by 8%. If this change was to happen and the gearbox was to be

removed, a new Ruland jaw would need to be ordered with a 6mm size to fix directly to

the motor instead of the gearbox shaft.

### 6.3. Bearing/Bush Discussion

Another change that could improve the design would be to use further bearings or

bushes to reduce the friction acting on the wing axle. Currently the wing axle rotates

inside the mechanism block with a 0.5mm clearance, this will involve resisting frictional

forces whereas if the axle instead rotated in bearings or low-friction bushes this will be

reduced. Although this would improve the efficiency of the design, a bearing with 20mm

ID would have a 32mm OD. This would require a far greater bore in the mechanism

block and lead to far more material waste, the additional costing of machining this bore

and purchasing these bearings was not justifiable for the current stage of my project. The mechanism block is also only 40mm wide leaving just 4mm thickness of material on

either side. Whilst aluminium would be sufficiently strong under this thickness, it is an

unnecessary risk to take.

### 6.4. Experimentation and Modelling

The experimentation that has been planned with this equipment has been outlined in

Section 2.4. The methodology and potential uses for the results were also discussed,

and the environments the rig was to be used in were also stated. Further analysis is

required for the design before testing, this is because there has yet to be a structural

assessment made on the response of the outer shaft under the 4.228Nm load that will be

experienced. Although the material properties and thickness show almost certain

structural strength, the task of an FEA analysis is relatively quick and simple and will be

greatly beneficial for peace of mind.

### 7. References:

[1] - C. Roh and M. Gharib, “Honeybees use their wings for water surface

locomotion,” Proceedings of the National Academy of Sciences, vol. 116, no. 49, pp.

24446–24451, Nov. 2019, doi: https://doi.org/10.1073/pnas.1908857116.

[2] – Becker, Florian. (2009). Variational Correlation and Decomposition Methods for

Particle Image Velocimetry. (accessed May 17, 2023).

[3] - D. L. Altshuler, W. B. Dickson, J. T. Vance, S. P. Roberts, and M. H. Dickinson,

“Short-amplitude high-frequency wing strokes determine the aerodynamics of honeybee

flight,” Proceedings of the National Academy of Sciences, vol. 102, no. 50, pp. 18213–

18218, Dec. 2005, doi: https://doi.org/10.1073/pnas.0506590102.

[4] - G. E. STRATTON, R. B. SUTER, and P. R. MILLER, “Evolution of water surface

locomotion by spiders: a comparative approach,” Biological Journal of the Linnean

Society, vol. 81, no. 1, pp. 63–78, Jan. 2004, doi: https://doi.org/10.1111/j.1095-

8312.2004.00269.x. (https://doi.org/10.1111/j.1095-8312.2004.00269.x)

[5] - L. Zhao, Q. Huang, X. Deng, and S. P. Sane, “Aerodynamic effects of flexibility in

flapping wings,” Journal of The Royal Society Interface, vol. 7, no. 44, pp. 485–497, Aug.

2009, doi: https://doi.org/10.1098/rsif.2009.0200.

[6] – A. Gehrke, G. Guyon-Crozier, and K. Mulleners, “Genetic Algorithm Based

Optimization of Wing Rotation in Hover,” Fluids, vol. 3, no. 3, p. 59, Aug. 2018, doi:

https://doi.org/10.3390/fluids3030059.

[7] – T.-T. Nguyen and D. Byun, “Two-Dimensional Aerodynamic Models of Insect Flight

for Robotic Flapping Wing Mechanisms of Maximum Efficiency,” Journal of Bionic

Engineering, vol. 5, no. 1, pp. 1–11, Mar. 2008, doi: https://doi.org/10.1016/s1672-

6529(08)60001-3.

[8] – A. Gehrke and K. Mulleners, “Phenomenology and scaling of optimal flapping wing

kinematics,” Bioinspiration & Biomimetics, vol. 16, no. 2, pp. 026016–026016, Jul. 2020,

doi: https://doi.org/10.1088/1748-3190/abd012.

[9] – S. A. Ansari, K. Knowles, and R. Zbikowski, “Insectlike Flapping Wings in the Hover

Part II: Effect of Wing Geometry,” Journal of Aircraft, vol. 45, no. 6, pp. 1976–1990, Nov.

2008, doi: https://doi.org/10.2514/1.35697.

[10] – A. Chaudhuri, R. T. Haftka, P. Ifju, K. Chang, C. Tyler, and T. Schmitz,

“Experimental flapping wing optimization and uncertainty quantification using limited

samples,” Structural and Multidisciplinary Optimization, vol. 51, no. 4, pp. 957–970, Nov.

2014, doi: https://doi.org/10.1007/s00158-014-1184-x.

[11] – A. R. Shanmugam and Chang Hwan Sohn, “Numerical investigation on thrust

production and unsteady mechanisms of three-dimensional oscillating wing,” Journal of

Mechanical Science and Technology, vol. 33, no. 12, pp. 5889–5900, Dec. 2019, doi:

https://doi.org/10.1007/s12206-019-1134-z.

[12] – D. Diaz-Arriba, T. Jardin, N. Gourdain, F. Pons, and L. David, “Experiments and

numerical simulations on hovering three-dimensional flexible flapping

wings,” Bioinspiration & Biomimetics, vol. 17, no. 6, p. 065006, Oct. 2022, doi:

https://doi.org/10.1088/1748-3190/ac8f06.

[13] – D. Diaz-Arriba, T. Jardin, N. Gourdain, F. Pons, and L. David, “Experiments and

numerical simulations on hovering three-dimensional flexible flapping

wings,” Bioinspiration & Biomimetics, vol. 17, no. 6, p. 065006, Oct. 2022, doi:

https://doi.org/10.1088/1748-3190/ac8f06.

[14] – W. R. Roderick, M. R. Cutkosky, and D. Lentink, “Touchdown to take-off: at the

interface of flight and surface locomotion,” Interface Focus, vol. 7, no. 1, pp. 20160094–

20160094, Feb. 2017, doi: https://doi.org/10.1098/rsfs.2016.0094.

[15] – S. K. CHATURVEDI, N. C. A. VISHWATH, H. VERMA, and T. MANCHANDA,

“Unmanned aero-amphibious vehicle: preliminary study on conceptual design,” INCAS

BULLETIN, vol. 11, no. 3, pp. 41–53, Sep. 2019, doi: https://doi.org/10.13111/2066-

8201.2019.11.3.4.

[16] – J. Izraelevitz and M. S. Triantafyllou, “A novel degree of freedom in flapping wings

shows promise for a dual aerial/aquatic vehicle propulsor,” arXiv (Cornell University),

May 2015, doi: https://doi.org/10.1109/icra.2015.7140015.

[17] – O. Ozcan, H. Wang, J. D. Taylor, and M. Sitti, “STRIDE II: A Water Strider-inspired

Miniature Robot with Circular Footpads,” International Journal of Advanced Robotic

Systems, vol. 11, no. 6, p. 85, Jan. 2014, doi: https://doi.org/10.5772/58701.

[18] – J. Moore, A. Fein, and W. Setzler, “Design and Analysis of a Fixed-Wing

Unmanned Aerial-Aquatic Vehicle,” 2018 IEEE International Conference on Robotics and

Automation (ICRA), May 2018, doi: https://doi.org/10.1109/icra.2018.8461240.

[19] – W. Weisler, W. Stewart, M. B. Anderson, K. J. Peters, A. Gopalarathnam, and M.

Bryant, “Testing and Characterization of a Fixed Wing Cross-Domain Unmanned Vehicle

Operating in Aerial and Underwater Environments,” IEEE Journal of Oceanic

Engineering, vol. 43, no. 4, pp. 969–982, Oct. 2018, doi:

https://doi.org/10.1109/joe.2017.2742798.

[20] – W. Stewart et al., “Design and demonstration of a seabird-inspired fixed-wing

hybrid UAV-UUV system,” Bioinspiration & Biomimetics, vol. 13, no. 5, p. 056013, Aug.

2018, doi: https://doi.org/10.1088/1748-3190/aad48b.

[21] – A. Villegas, V. Mishkevich, Y. Gulak, and F. J. Diez, “Analysis of key elements to

evaluate the performance of a multirotor unmanned aerial–aquatic vehicle,” Aerospace

Science and Technology, vol. 70, pp. 412–418, Nov. 2017, doi:

https://doi.org/10.1016/j.ast.2017.07.046.

[22] – D. Lu et al., “Design, fabrication, and characterization of a multimodal hybrid aerial

underwater vehicle,” Ocean Engineering, vol. 219, p. 108324, Jan. 2021, doi:

https://doi.org/10.1016/j.oceaneng.2020.108324.

[23] – A. Farinha, Julien di Tria, R. Zufferey, S. F. Armanini, and M. Kovac, “Challenges

in Control and Autonomy of Unmanned Aerial-Aquatic Vehicles,” Mediterranean

Conference on Control and Automation, Jun. 2021, doi:

https://doi.org/10.1109/med51440.2021.9480342.

[24] – Xinyan Deng, L. Schenato, Wei Chung Wu, and S. S. Sastry, “Flapping flight for

biomimetic robotic insects: part I-system modeling,” IEEE Transactions on Robotics, vol.

22, no. 4, pp. 776–788, Aug. 2006, doi: https://doi.org/10.1109/tro.2006.875480.

[25] – Y. M. Chukewad, J. James, A. Singh, and S. Fuller, “RoboFly: An Insect-Sized

Robot With Simplified Fabrication That Is Capable of Flight, Ground, and Water Surface

Locomotion,” IEEE Transactions on Robotics, vol. 37, no. 6, pp. 2025–2040, Dec. 2021,

doi: https://doi.org/10.1109/tro.2021.3075374.

[26] – P. Gopalakrishnan and D. K. Tafti, “Effect of Wing Flexibility on Lift and Thrust

Production in Flapping Flight,” AIAA Journal, vol. 48, no. 5, pp. 865–877, May 2010, doi:

https://doi.org/10.2514/1.39957.

[27] – T. Hesselberg, “Sensors and control systems for micro‐air vehicles: lessons from

flies,” Sensor Review, vol. 29, no. 2, pp. 120–126, Mar. 2009, doi:

https://doi.org/10.1108/02602280910936228.

[28] – “STM23S-3RE | Applied Motion,” www.applied-motion.com. https://www.applied-

motion.com/products/integrated-steppers/stm23s-3re (accessed May 03, 2023).

[29] – “M201624 2 MOD - 1.5 Ratio - 16/24 Teeth Metric Precision Bevel Gears - Steel

EN8,” Bolton Engineering Products Ltd - Bearing, Power Transmission & Workwear

Supplier. https://bepltd.com/products/2-mod-1-5-ratio-16-24-teeth-precision-bevel-gears-

steel-en8 (accessed May 03, 2023).

[30] – “ATI Industrial Automation: F/T Sensor Nano17,” www.ati-ia.com. https://www.ati-

ia.com/products/ft/ft_models.aspx?id=Nano17 (https://www.ati-ia.com/products/ft/ft_models.aspx?id=Nano17)

[31] – “RE PLANETARY GEARBOX RE34 PLANETARY GEARBOX.” Accessed: May

04, 2023. [Online]. Available:

https://motioncontrolproducts.com/media/productattach/r/e/re-planetary-gearbox.pdf

[32] – “Jaw Couplings: Curved for Zero-Backlash | Ruland,” Ruland.com, 2015.

https://www.ruland.com/servo-couplings/jaw-couplings.html (accessed Nov. 10, 2019).

[33] – Properties: Stainless Steel - Grade 316 (UNS S31600, “Properties: Stainless Steel
- Grade 316 (UNS S31600),” AZoM.com, 2019.

https://www.azom.com/properties.aspx?ArticleID=863

[34] – “Aluminum,” www.mit.edu. https://www.mit.edu/~6.777/matprops/aluminum.htm
[35] – Wake structure and aerodynamic performance of low aspect-ratio revolving plates

at low reynolds number - Scientific Figure on ResearchGate. Available from:

https://www.researchgate.net/figure/a-Lift-and-drag-coefficient-of-rotational-cases-for-a-

rectangular-plate-of-AR2-at_fig4_286411007 (accessed 3 May, 2023)

[36] – “Torsion of a Shaft under the Action of Two Torques,” autofem.com.

https://autofem.com/examples/torsion_of_shaft_with_circular_cross_section_under_2_to

rques.html (https://autofem.com/examples/torsion_of_shaft_with_circular_cross_section_under_2_torques.html)

[37] – Mouser, “Connective Peripherals ES-U-3001-M,” Mouser Electronics, 2023.

https://www.mouser.co.uk/ProductDetail/Connective-Peripherals/ES-U-3001-

M?qs=jotIDw4kbYV9GiEaKLbLDA%3D%3D (accessed May 18, 2023).

[38] – ATI, “F/T Sensor Data Acquisition (DAQ) Systems.” https://www.ati-

ia.com/app_content/documents/9620-05-DAQ.pdf (accessed May 18, 2023).

[39] – “Simply Bearings Ltd,” simplybearings.co.uk.

https://simplybearings.co.uk/shop/p20194084/P12-5M-15F-5mm-Pitch-12-Tooth-

Flanged-HTD-Type-Steel-Timing-Pulley-for-15mm-Wide-Belts/product_info.html

(accessed May 03, 2023).

[40] – “4 Hole Flange Bearing Unit 30mm ID | RS,” uk.rs-online.com. https://uk.rs-

online.com/web/p/bearing-units/7508784 (accessed May 04, 2023).
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

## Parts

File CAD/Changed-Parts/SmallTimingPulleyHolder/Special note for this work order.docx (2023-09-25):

Special note for this work order:

1. No new material is needed. The student will drop-off the steel rod to be machined at the EDMC once their supervisor has approved the quotation.
2. Work description:
  a. Steel rod outer diameter reduced to 6.5mm for a length of 60mm from one end. (See drawing)
  b. Either end is fine.
3. If more dimensions are needed, or if the drawing is unclear, please contact the student at:
  a. kwl1y19@soton.ac.uk or
  b. +44 07778147127

Thank you!

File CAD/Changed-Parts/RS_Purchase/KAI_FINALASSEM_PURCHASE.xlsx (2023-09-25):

Category | Vendor | PN | Item | UoM | Qty | Price per unit (inc. VAT) | Sub-Total | Link
Fixtures | RS-PRO | 183-8604 | Button Head Socket M3 | Box of 100 | 1 | £15.62 | £15.62 | https://uk.rs-online.com/web/p/socket-screws/1838604?gb=b
 | RS-PRO | LH M3X10 | Yahata Neji Cross Truss Iron Machine Screws, M3x10mm | Bag of 100 | 1 | £7.06 | £7.06 | https://uk.rs-online.com/web/p/machine-screws/6644962?matchtype=&pla-339504726200&gclsrc=aw.ds
 | RS-PRO | M5X20 | Yahata Neji Black Oxide Steel Hex Socket Cap Screw, M5 x 20mm | Box of 100 | 1 | £12.47 | £12.47 | https://uk.rs-online.com/web/p/socket-screws/4733681?gb=b
 | RS-PRO | M6X20 | Yahata Neji Black Oxide Steel Hex Socket Cap Screw, M6 x 20mm | Box of 100 | 1 | £12.47 | £12.47 | https://uk.rs-online.com/web/p/socket-screws/4733754?gb=b
Cables and Connectors | RS-PRO | 222-4315 | Hew Heinz Eilentropp SIFF Series Red 0.52 mm² Hook Up Wire, 20 AWG, 270/0.05 mm, 5m, Silicone Insulation | Reel of 5m | 1 | £21.20 | £21.20 | https://uk.rs-online.com/web/p/hook-up-wire/2224315?gb=b
 | RS-PRO | 222-4270 | Hew Heinz Eilentropp SIFF Series Black 0.52 mm² Hook Up Wire, 20 AWG, 270/0.05 mm, 5m, Silicone Insulation | Reel of 5m | 1 | £21.20 | £21.20 | https://uk.rs-online.com/web/p/hook-up-wire/2224270?gb=b
 | RS-PRO | 180-6650 | RS PRO 4 mm Red Male Banana Connectors - Screw Termination, 50V, 10A | Each | 2 | £0.98 | £1.96 | https://uk.rs-online.com/web/p/banana-connectors/1806650?gb=b
 | RS-PRO | 180-6649 | RS PRO 4 mm Black Male Banana Connectors - Screw Termination, 50V, 10A | Each | 2 | £1.06 | £2.12 | https://uk.rs-online.com/web/p/banana-connectors/1806649?gb=b
 | RS-PRO | 236-9076 | RS PRO USB 2.0 Cable, Male USB A to Male USB B Cable, 3m | Each | 1 | £2.99 | £2.99 | https://uk.rs-online.com/web/p/usb-cables/2369076?matchtype=&aud-842313741498:pla-363628110714&gclsrc=aw.ds
 | Digikey | 1881354 | Phoenix Contact TERM BLOCK PLUG 5POS STR 2.5MM | Each | 2 | £5.16 | £10.32 | https://www.digikey.co.uk/en/products/detail/phoenix-contact/1881354/308238?s=N4IgTCBcDaIIwA4FwMwFYAsIC6BfIA
 | Digikey | 1615780000 | Weidmüller TERM BLOCK PLUG 2POS STR 3.5MM | Each | 2 | £2.68 | £5.36 | https://www.digikey.co.uk/en/products/detail/weidm%C3%BCller/1615780000/263668?s=N4IgTCBcDaIIwDY4FYDsAOADNzIC6AvkA
Serial Adapter | thepihut.com |  | USB to RS485/422 Industrial Grade Isolated Converter | Each | 1 | £17.40 | £17.40 | https://thepihut.com/products/usb-to-rs485-422-industrial-grade-isolated-converter?variant=42426283425987&currency=GBP
Total |  |  |  |  |  |  | £130.17

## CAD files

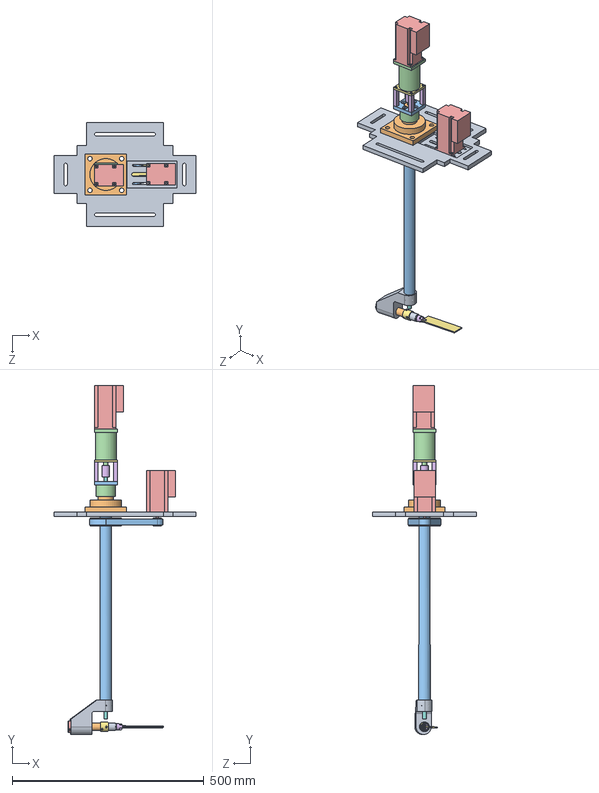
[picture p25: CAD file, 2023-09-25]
CAD/Original_Parts/Full assembly.SLDASM
370.0 x 910.0 x 270.0 mm
Mounting plates bottom piece
shaft bearing
Outer shaft
shaft-flange coupler
axle end cap
Gearbox mount spacer x 4
Gearbox plate
Inner shaft
mechanism block bolton gears
Wing Axle
Outer Shaft Flange plate
gearbox
motor x 2
inner shaft-gearbox coupler
sensor to axle Coupler
ATI nano 17 back adapter IP68 holes
Nano17 ip68
alignment bearings x 2
belt
driving pulley
shaft pulley
Wing adapter
Wing plate#

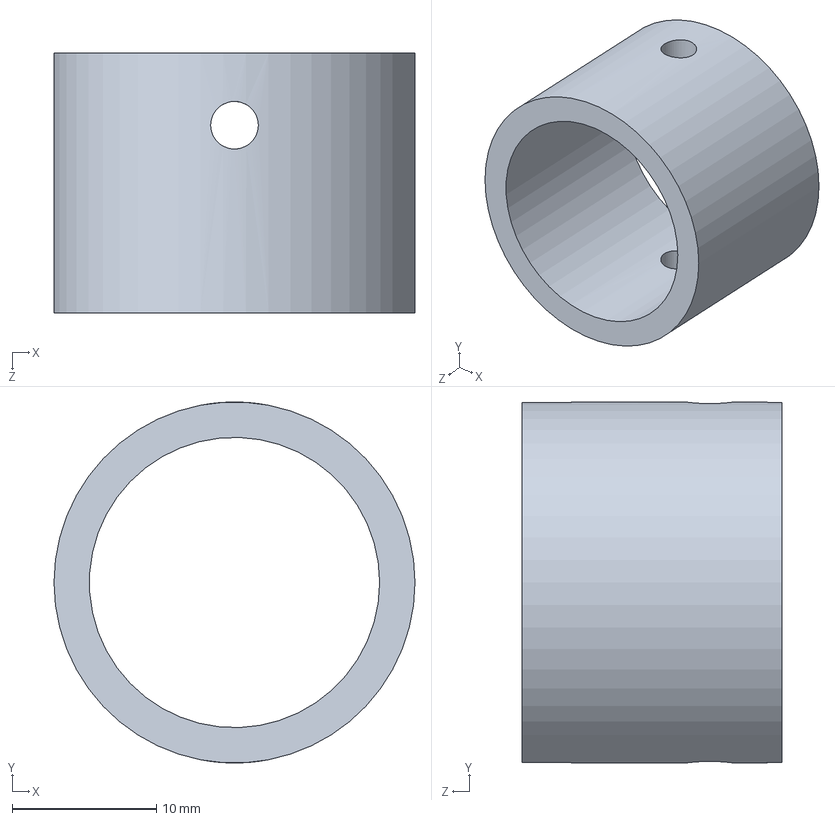
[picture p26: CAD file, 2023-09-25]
CAD/Changed-Parts/GearFaceRemachining/Part1.SLDPRT
25.0 x 25.0 x 18.0 mm

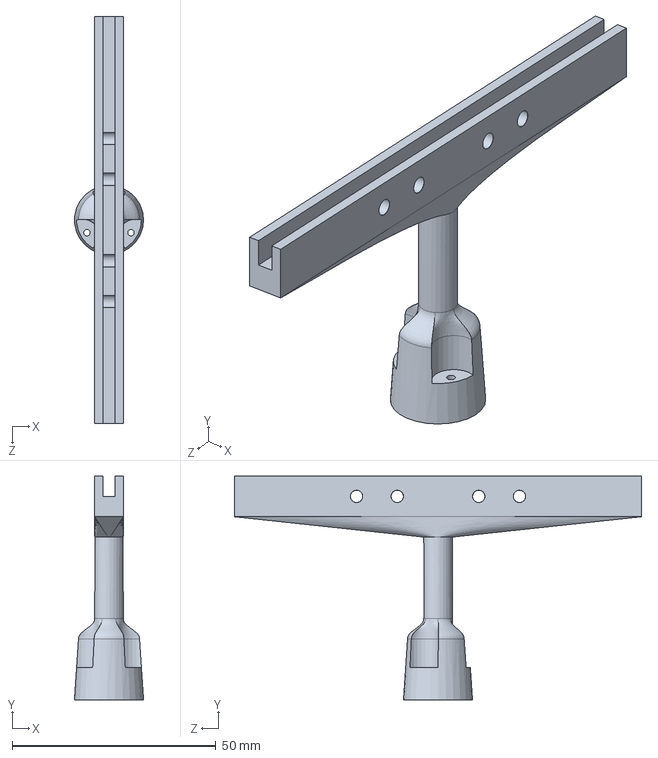
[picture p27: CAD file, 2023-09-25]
CAD/Changed-Parts/HeavePlateAdapter/Wing adapter.SLDPRT
17.0 x 55.0 x 100.0 mm

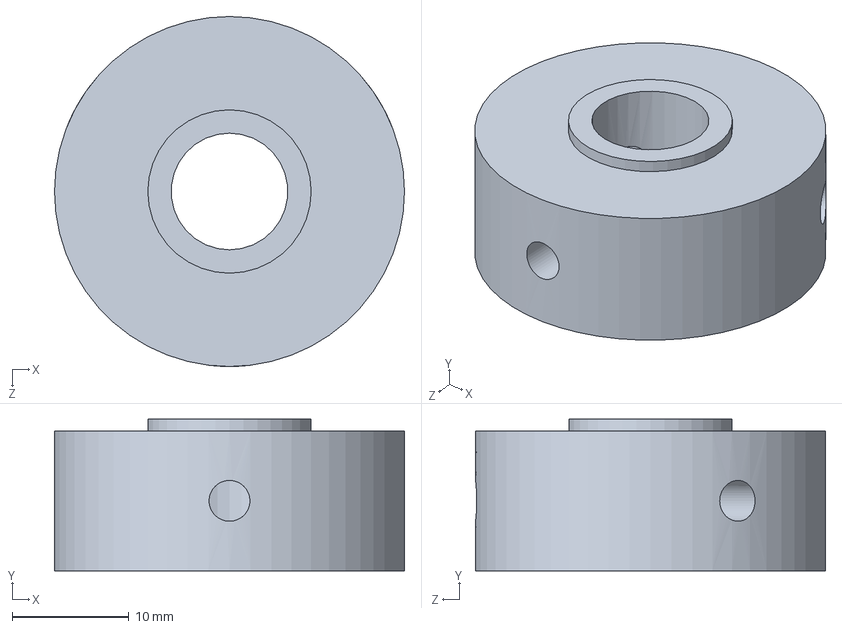
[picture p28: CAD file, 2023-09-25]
CAD/Changed-Parts/InnerRodRetention/InnerRodRetentionRing.SLDPRT
30.0 x 13.0 x 30.0 mm

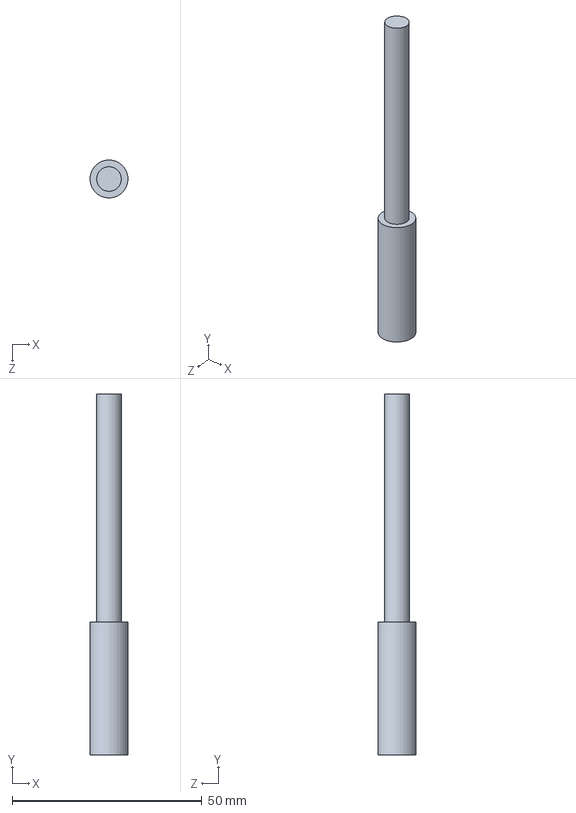
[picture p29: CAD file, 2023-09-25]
CAD/Changed-Parts/SmallTimingPulleyHolder/SmallTimingPulleyAdapter_v2.SLDPRT
9.99 x 95.0 x 10.0 mm

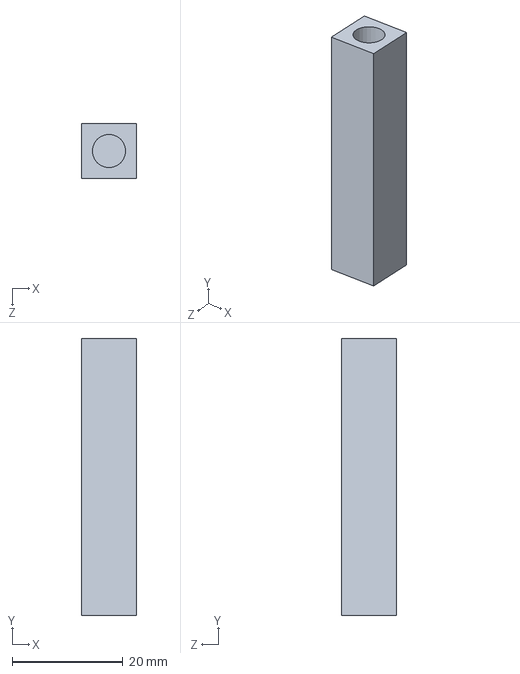
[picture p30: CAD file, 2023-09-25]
CAD/Original_Parts/Gearbox mount spacer.SLDPRT
10.0 x 50.0 x 10.0 mm

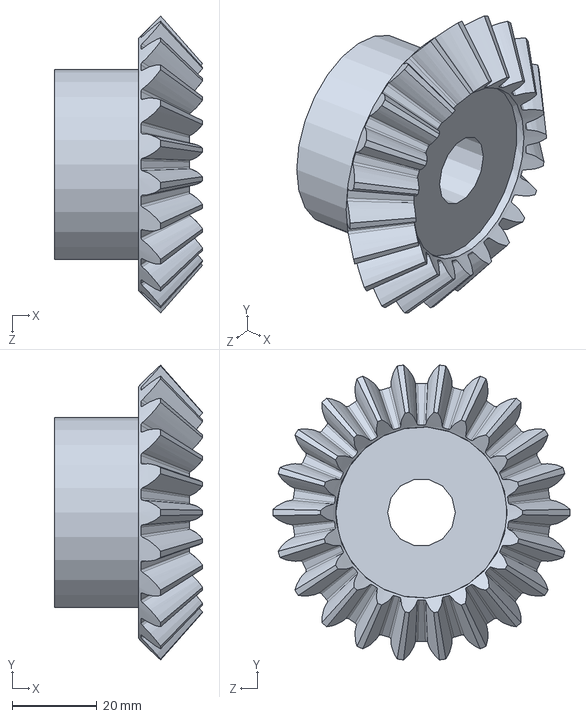
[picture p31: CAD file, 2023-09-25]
CAD/Changed-Parts/GearFaceRemachining/driving bevel gear.SLDPRT
35.0 x 69.7 x 70.2 mm

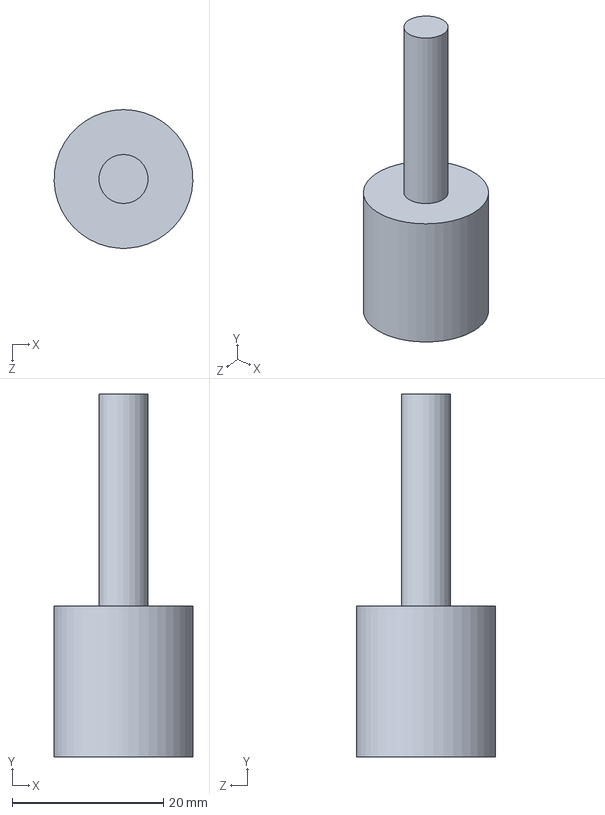
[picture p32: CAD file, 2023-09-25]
CAD/Changed-Parts/SmallTimingPulleyHolder/SmallTimingPulleyHolder.SLDPRT
18.3 x 48.0 x 18.4 mm

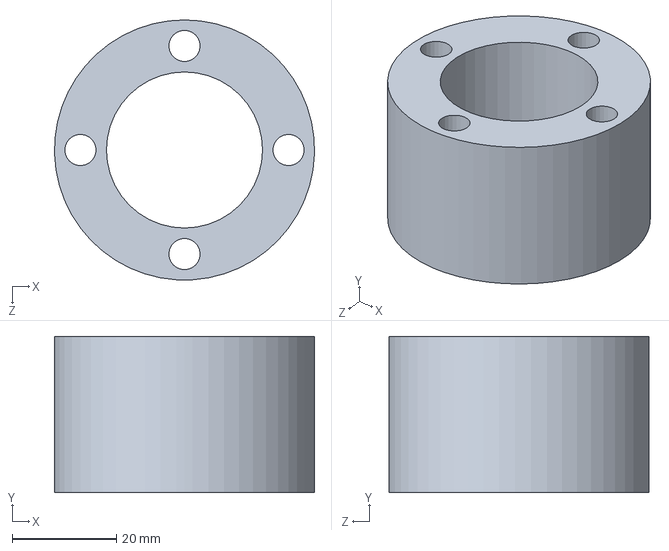
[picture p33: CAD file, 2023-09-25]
CAD/Original_Parts/shaft-flange coupler.SLDPRT
50.0 x 30.0 x 50.0 mm

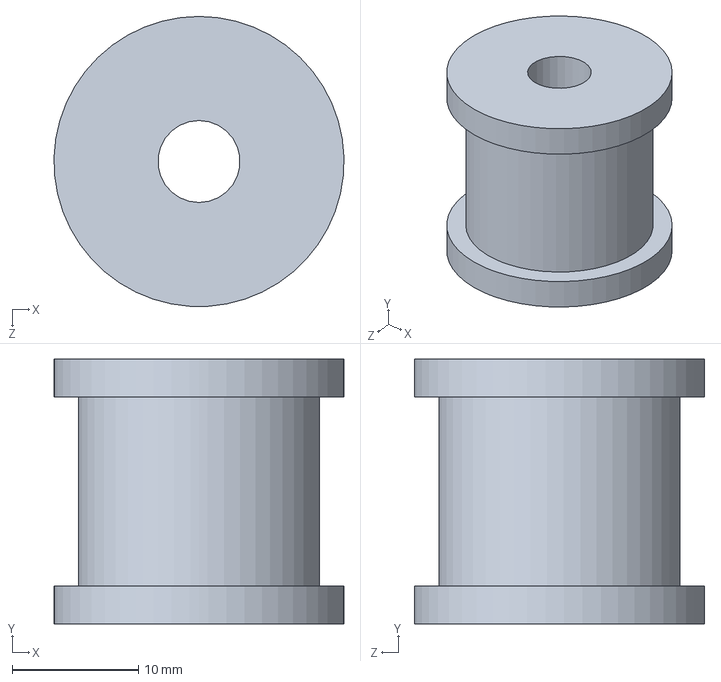
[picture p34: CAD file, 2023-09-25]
CAD/Original_Parts/driving pulley.SLDPRT
23.0 x 21.0 x 23.0 mm

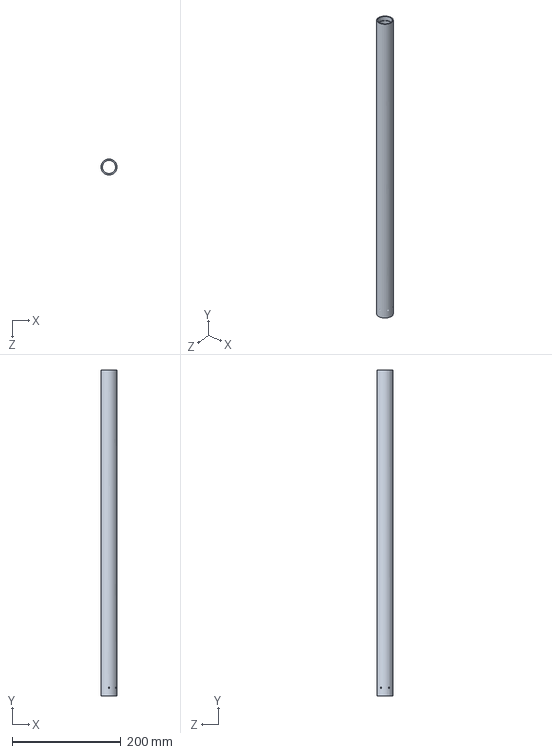
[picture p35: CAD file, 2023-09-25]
CAD/Original_Parts/Outer shaft.SLDPRT
29.5 x 600.0 x 29.5 mm

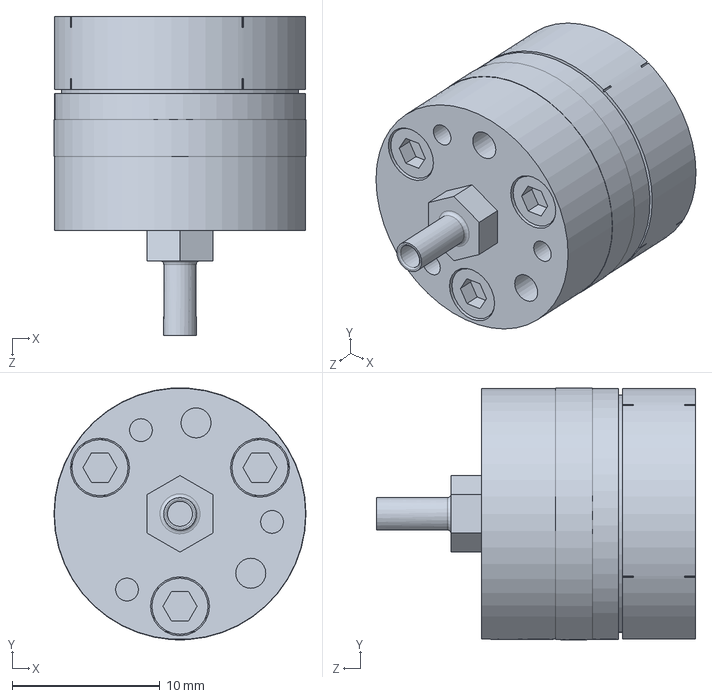
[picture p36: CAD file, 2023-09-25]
CAD/Original_Parts/ATI nano 17.SLDPRT
17.0 x 17.0 x 21.6 mm

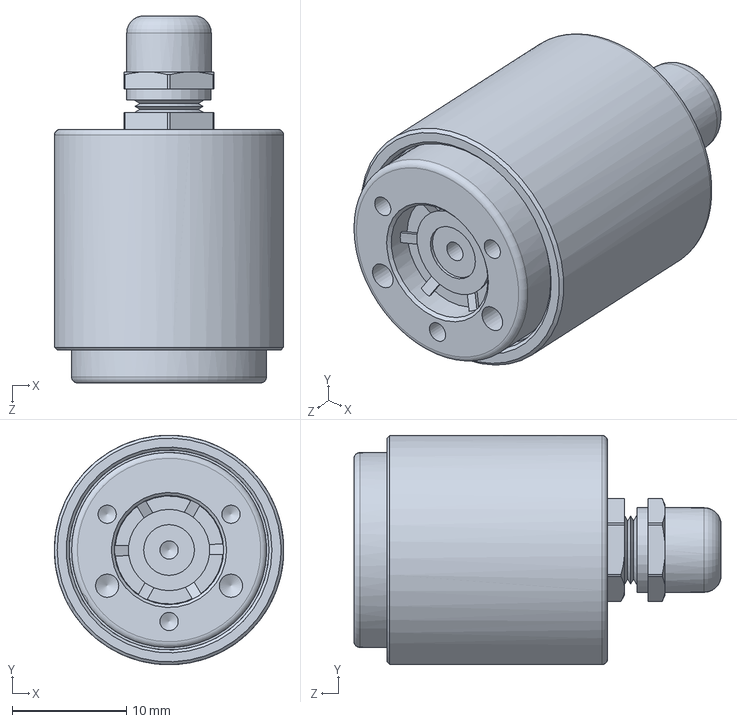
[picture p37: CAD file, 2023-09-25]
CAD/Original_Parts/Nano17 ip68.SLDPRT
20.1 x 20.1 x 32.1 mm

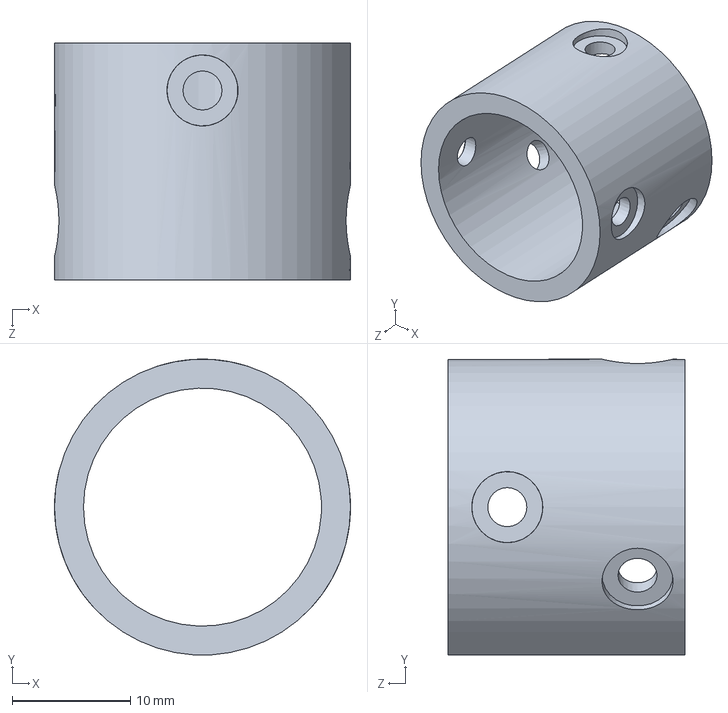
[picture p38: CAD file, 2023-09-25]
CAD/Original_Parts/sensor to axle Coupler.SLDPRT
25.0 x 25.0 x 20.0 mm

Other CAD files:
CAD/Changed-Parts/MountingPlatform/aluminum_beam.SLDPRT
CAD/Original_Parts/driving bevel gear.SLDPRT
CAD/Original_Parts/shaft pulley.SLDPRT
CAD/Original_Parts/ATI nano 17 back adapter.SLDPRT
CAD/Changed-Parts/GearFaceRemachining/A1_Student_Drawing.slddrw
CAD/Changed-Parts/GearFaceRemachining/A2_Student_Drawing.slddrw
CAD/Changed-Parts/GearFaceRemachining/A3_Student_Drawing.slddrw
CAD/Changed-Parts/GearFaceRemachining/GearFaceRemachining.SLDDRW
CAD/Changed-Parts/SmallTimingPulleyHolder/SmallTimingPulleyAdapter.SLDDRW
CAD/Changed-Parts/TubeRemachining/KWL-31311466_TubeRemachining.SLDDRW
CAD/Original_Parts/ATI nano 17 back adapter IP68 holes.SLDPRT
CAD/Original_Parts/Gearbox plate.SLDPRT
CAD/Original_Parts/Inner shaft.SLDPRT
CAD/Original_Parts/Mounting plates bottom piece.SLDPRT
CAD/Original_Parts/Outer Shaft Flange plate.SLDPRT
CAD/Original_Parts/Outer shaft.SLDDRW
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

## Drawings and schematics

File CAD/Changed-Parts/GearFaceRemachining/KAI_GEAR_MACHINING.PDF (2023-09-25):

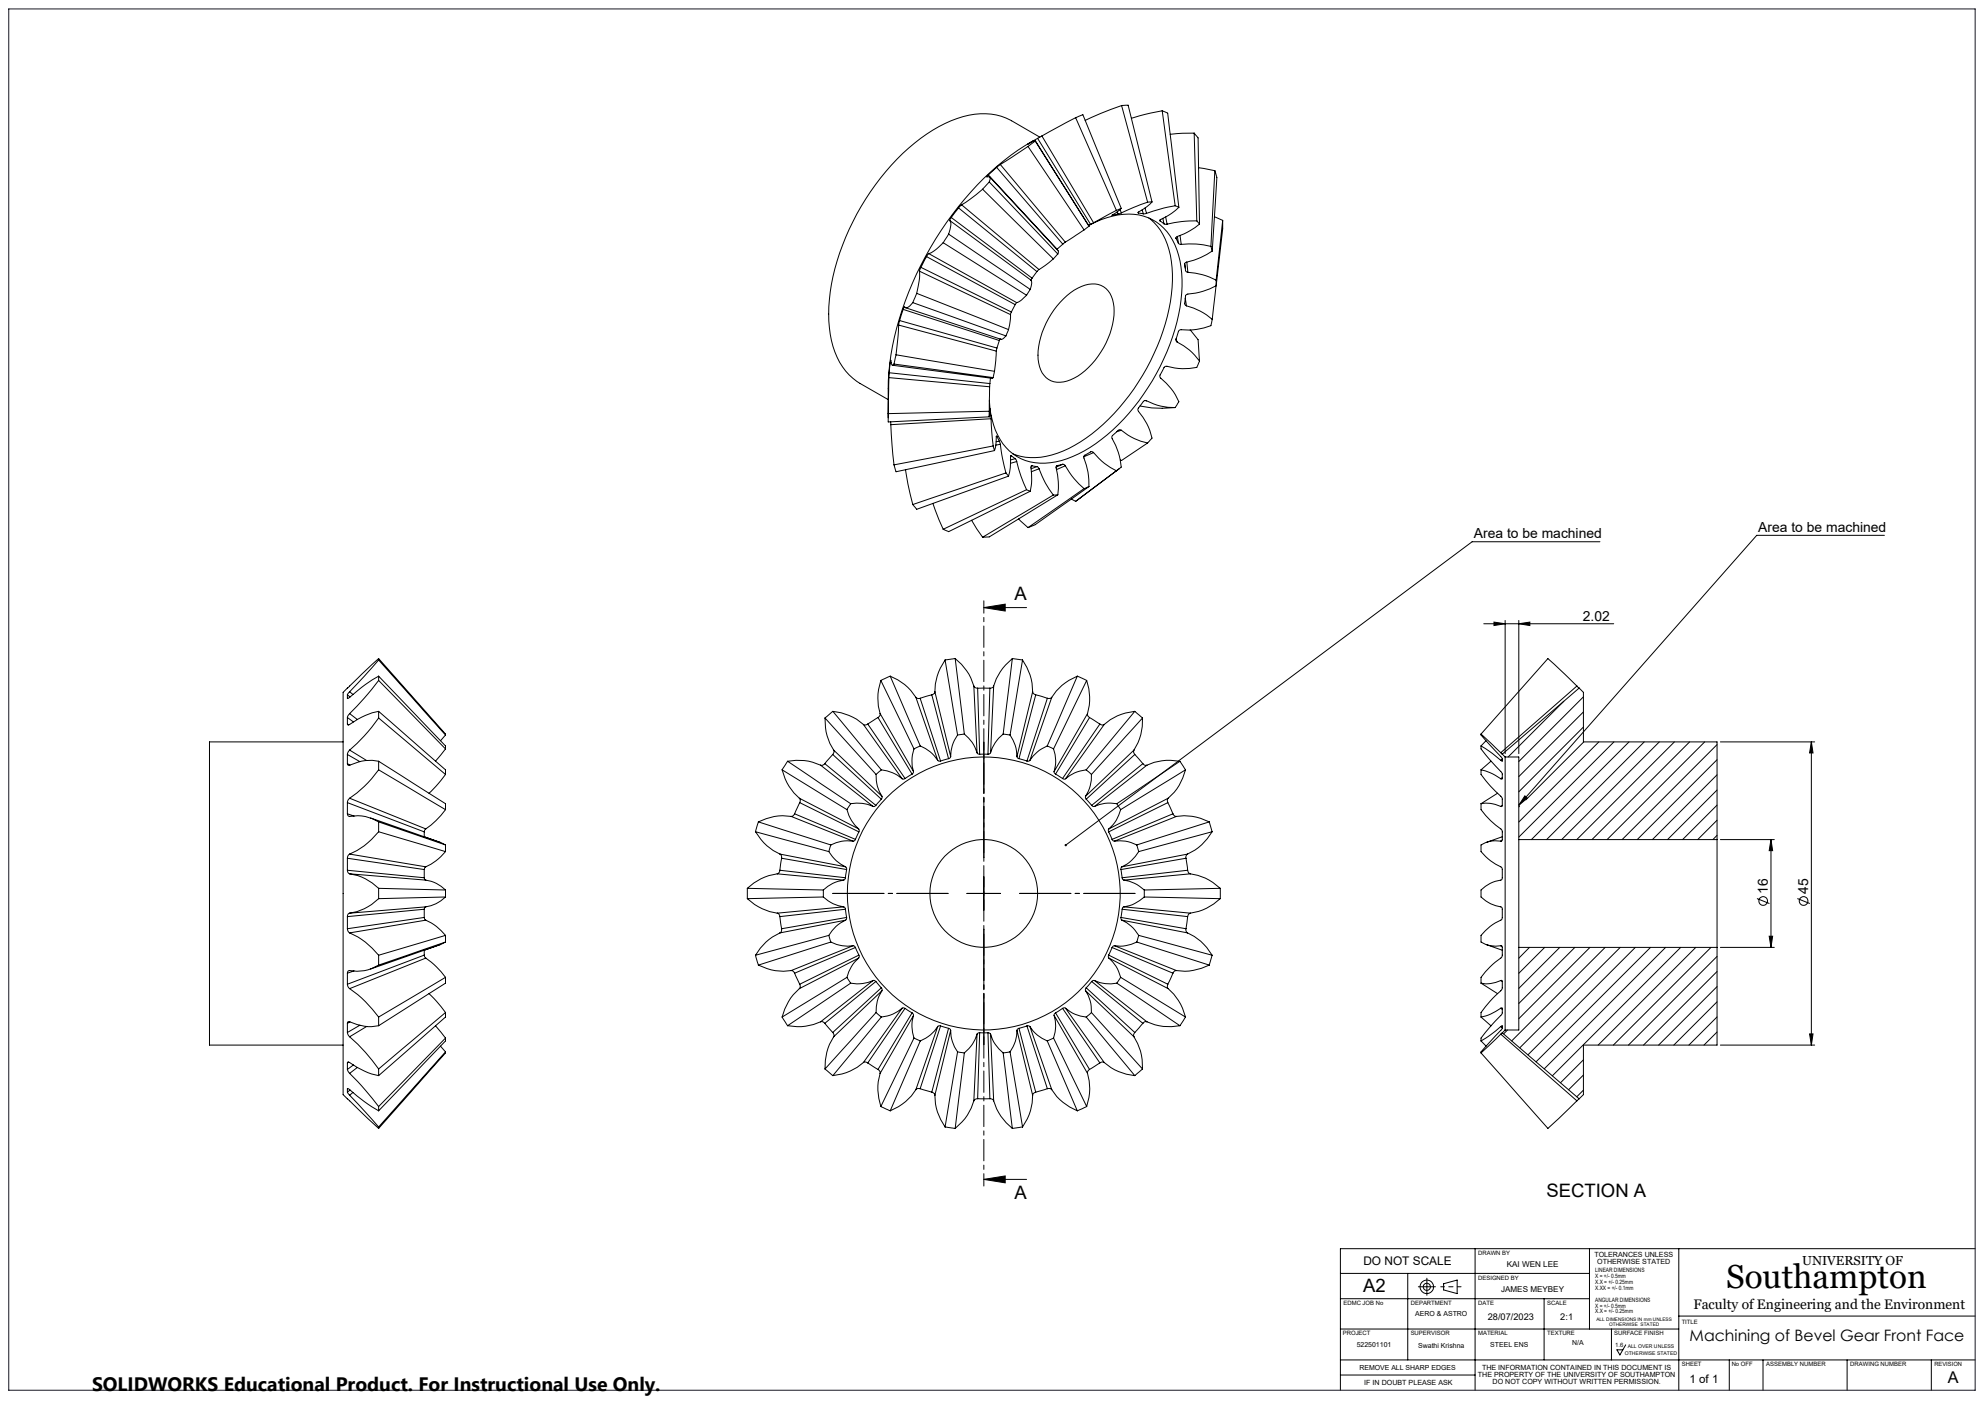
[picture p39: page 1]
SECTION A; Swathi Krishna; STEEL ENS; AERO & ASTRO; JAMES MEYBEY; SHEET; No OFF; ASSEMBLY NUMBER; DRAWING NUMBER; REVISION; PROJECT; SUPERVISOR; MATERIAL; TEXTURE; SURFACE FINISH; DESIGNED BY; EDMC JOB No; DEPARTMENT; DATE; SCALE; OTHERWISE STATED

Area to be machined

DRAWN BY
KAI WEN LEE

TOLERANCES UNLESS
OTHERWISE STATED
LINEAR DIMENSIONS
Faculty of Engineering and the Environment ALL DIMENSIONS IN mm UNLESS
ANGULAR DIMENSIONS

DO NOT SCALE

Southampton UNIVERSITY OF

TITLE
Machining of Bevel Gear Front Face

ALL OVER UNLESS

SOLIDWORKS Educational Product. For Instructional Use Only.

REMOVE ALL SHARP EDGES
IF IN DOUBT PLEASE ASK

THE INFORMATION CONTAINED IN THIS DOCUMENT IS
THE PROPERTY OF THE UNIVERSITY OF SOUTHAMPTON
DO NOT COPY WITHOUT WRITTEN PERMISSION.

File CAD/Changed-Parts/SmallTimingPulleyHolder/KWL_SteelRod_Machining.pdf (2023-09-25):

Area to be machined | 6.50 60

1.75

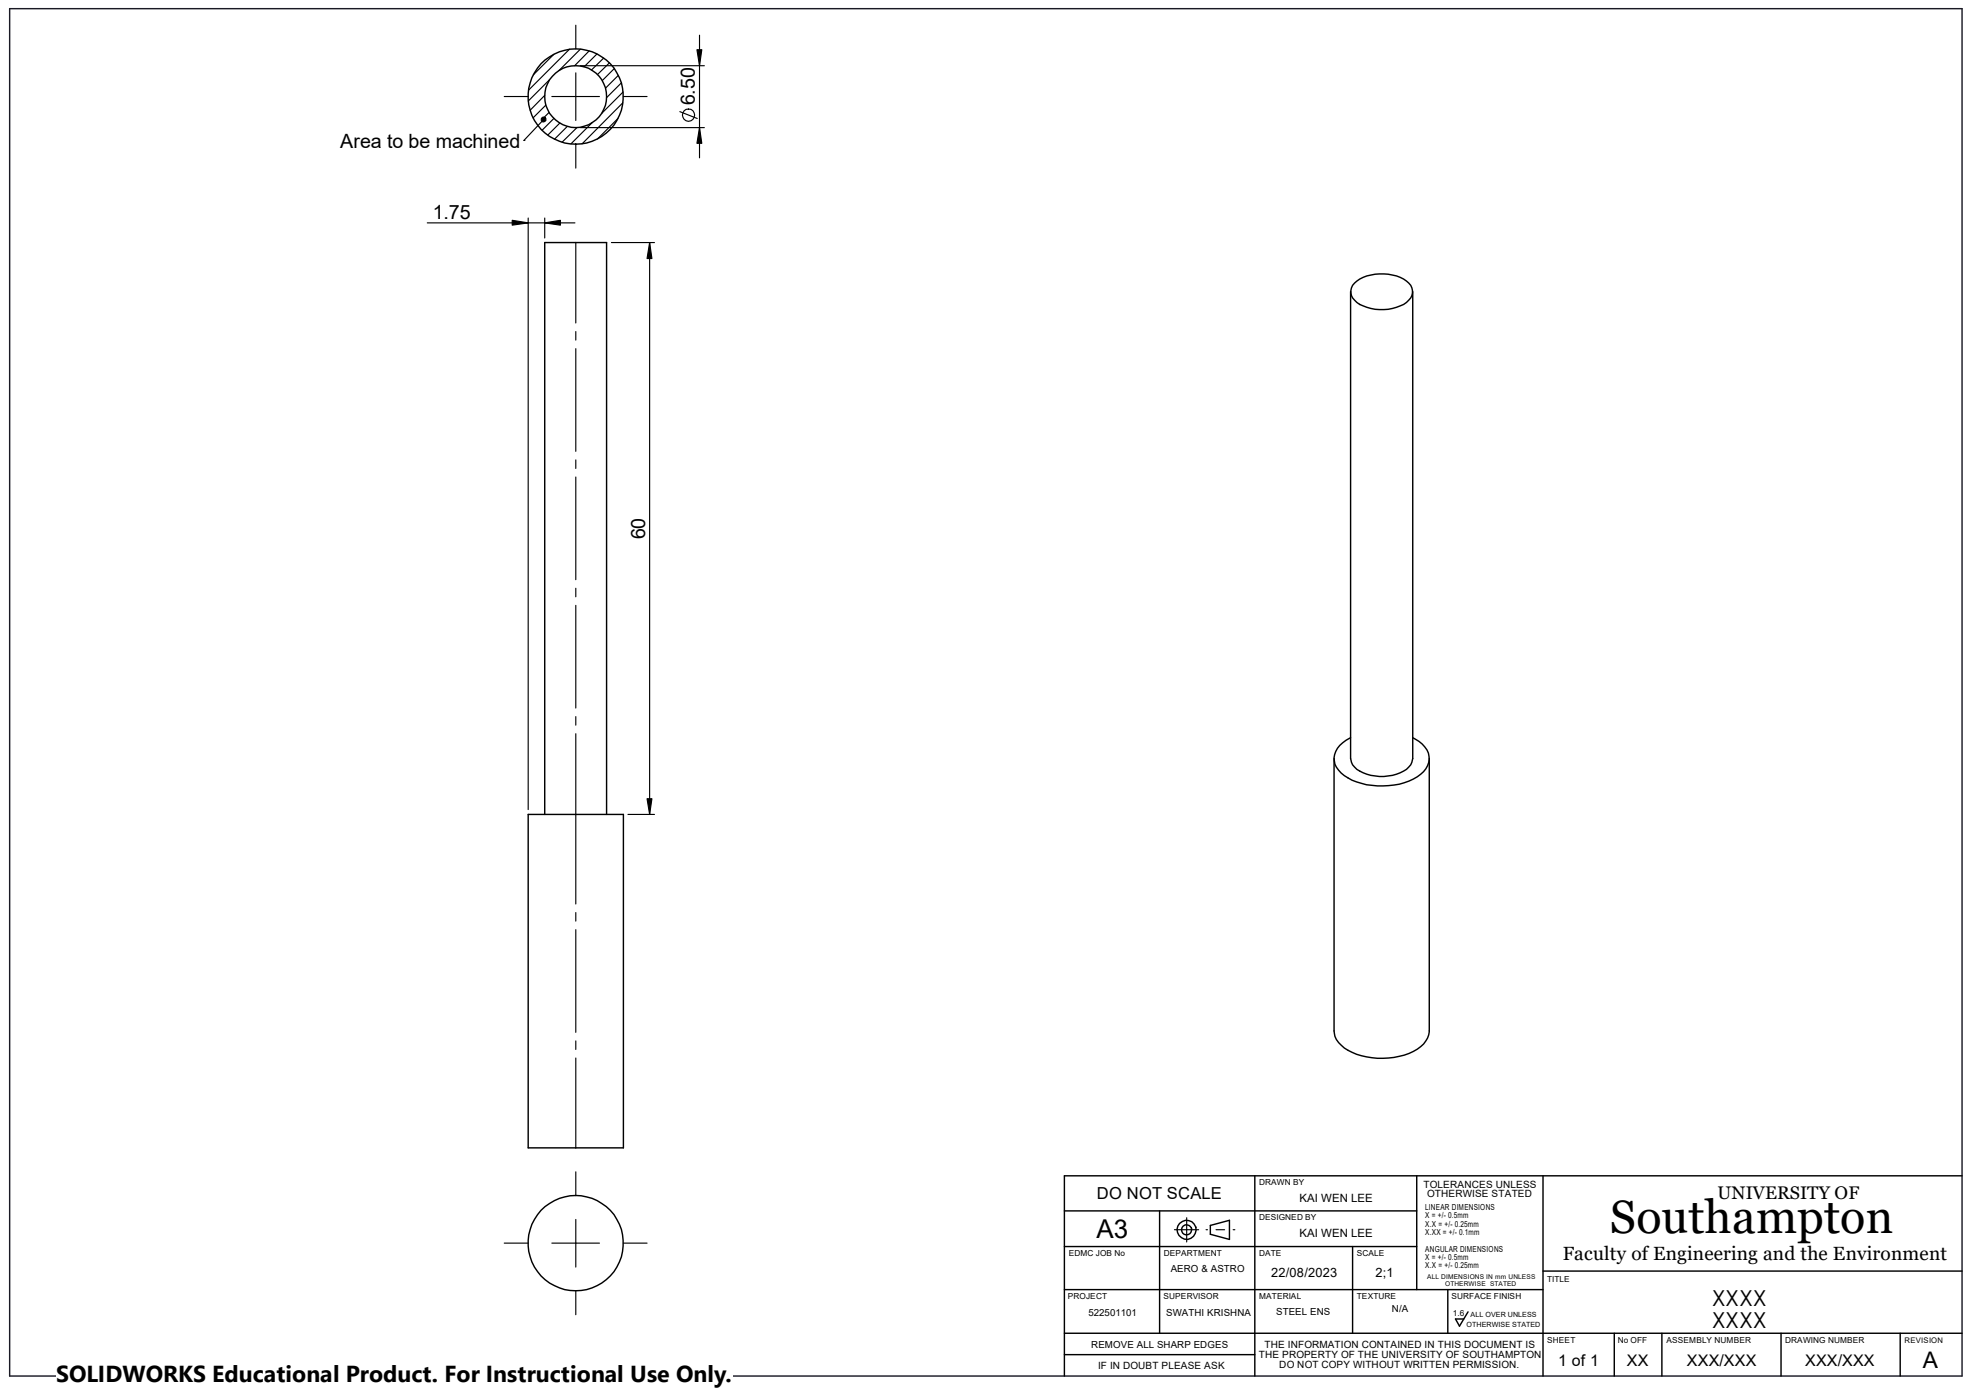
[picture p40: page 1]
TITLE; XXXX

DO NOT SCALE | DRAWN BY KAI WEN LEE | TOLERANCES UNLESS OTHERWISE STATED X = +/- 0.5mm X.X = +/- 0.25mm X.XX = +/- 0.1mm ANGULAR DIMENSIONS X = +/- 0.5mm ALL DIMENSIONS IN mm UNLESS OTHERWISE STATED | Southampton UNIVERSITY OF Faculty of Engineering and the Environment

EDMC JOB No | DEPARTMENT | THE PROPERTY OF THE UNIVERSITY OF SOUTHAMPTON LINEAR DIMENSIONS DATE 22/08/2023 | SCALE 2;1 | X.X = +/- 0.25mm AERO & ASTRO
A3 | | | | DESIGNED BY KAI WEN LEE

PROJECT 522501101 | SUPERVISOR SWATHI KRISHNA | MATERIAL STEEL ENS | TEXTURE N/A | SURFACE FINISH 1.6 ALL OVER UNLESS OTHERWISE STATED

REMOVE ALL SHARP EDGES | THE INFORMATION CONTAINED IN THIS DOCUMENT IS DO NOT COPY WITHOUT WRITTEN PERMISSION. | SHEET 1 of 1 | No OFF XX | ASSEMBLY NUMBER XXX/XXX | DRAWING NUMBER XXX/XXX | REVISION A

SOLIDWORKS Educational Product. For Instructional Use Only.

IF IN DOUBT PLEASE ASK

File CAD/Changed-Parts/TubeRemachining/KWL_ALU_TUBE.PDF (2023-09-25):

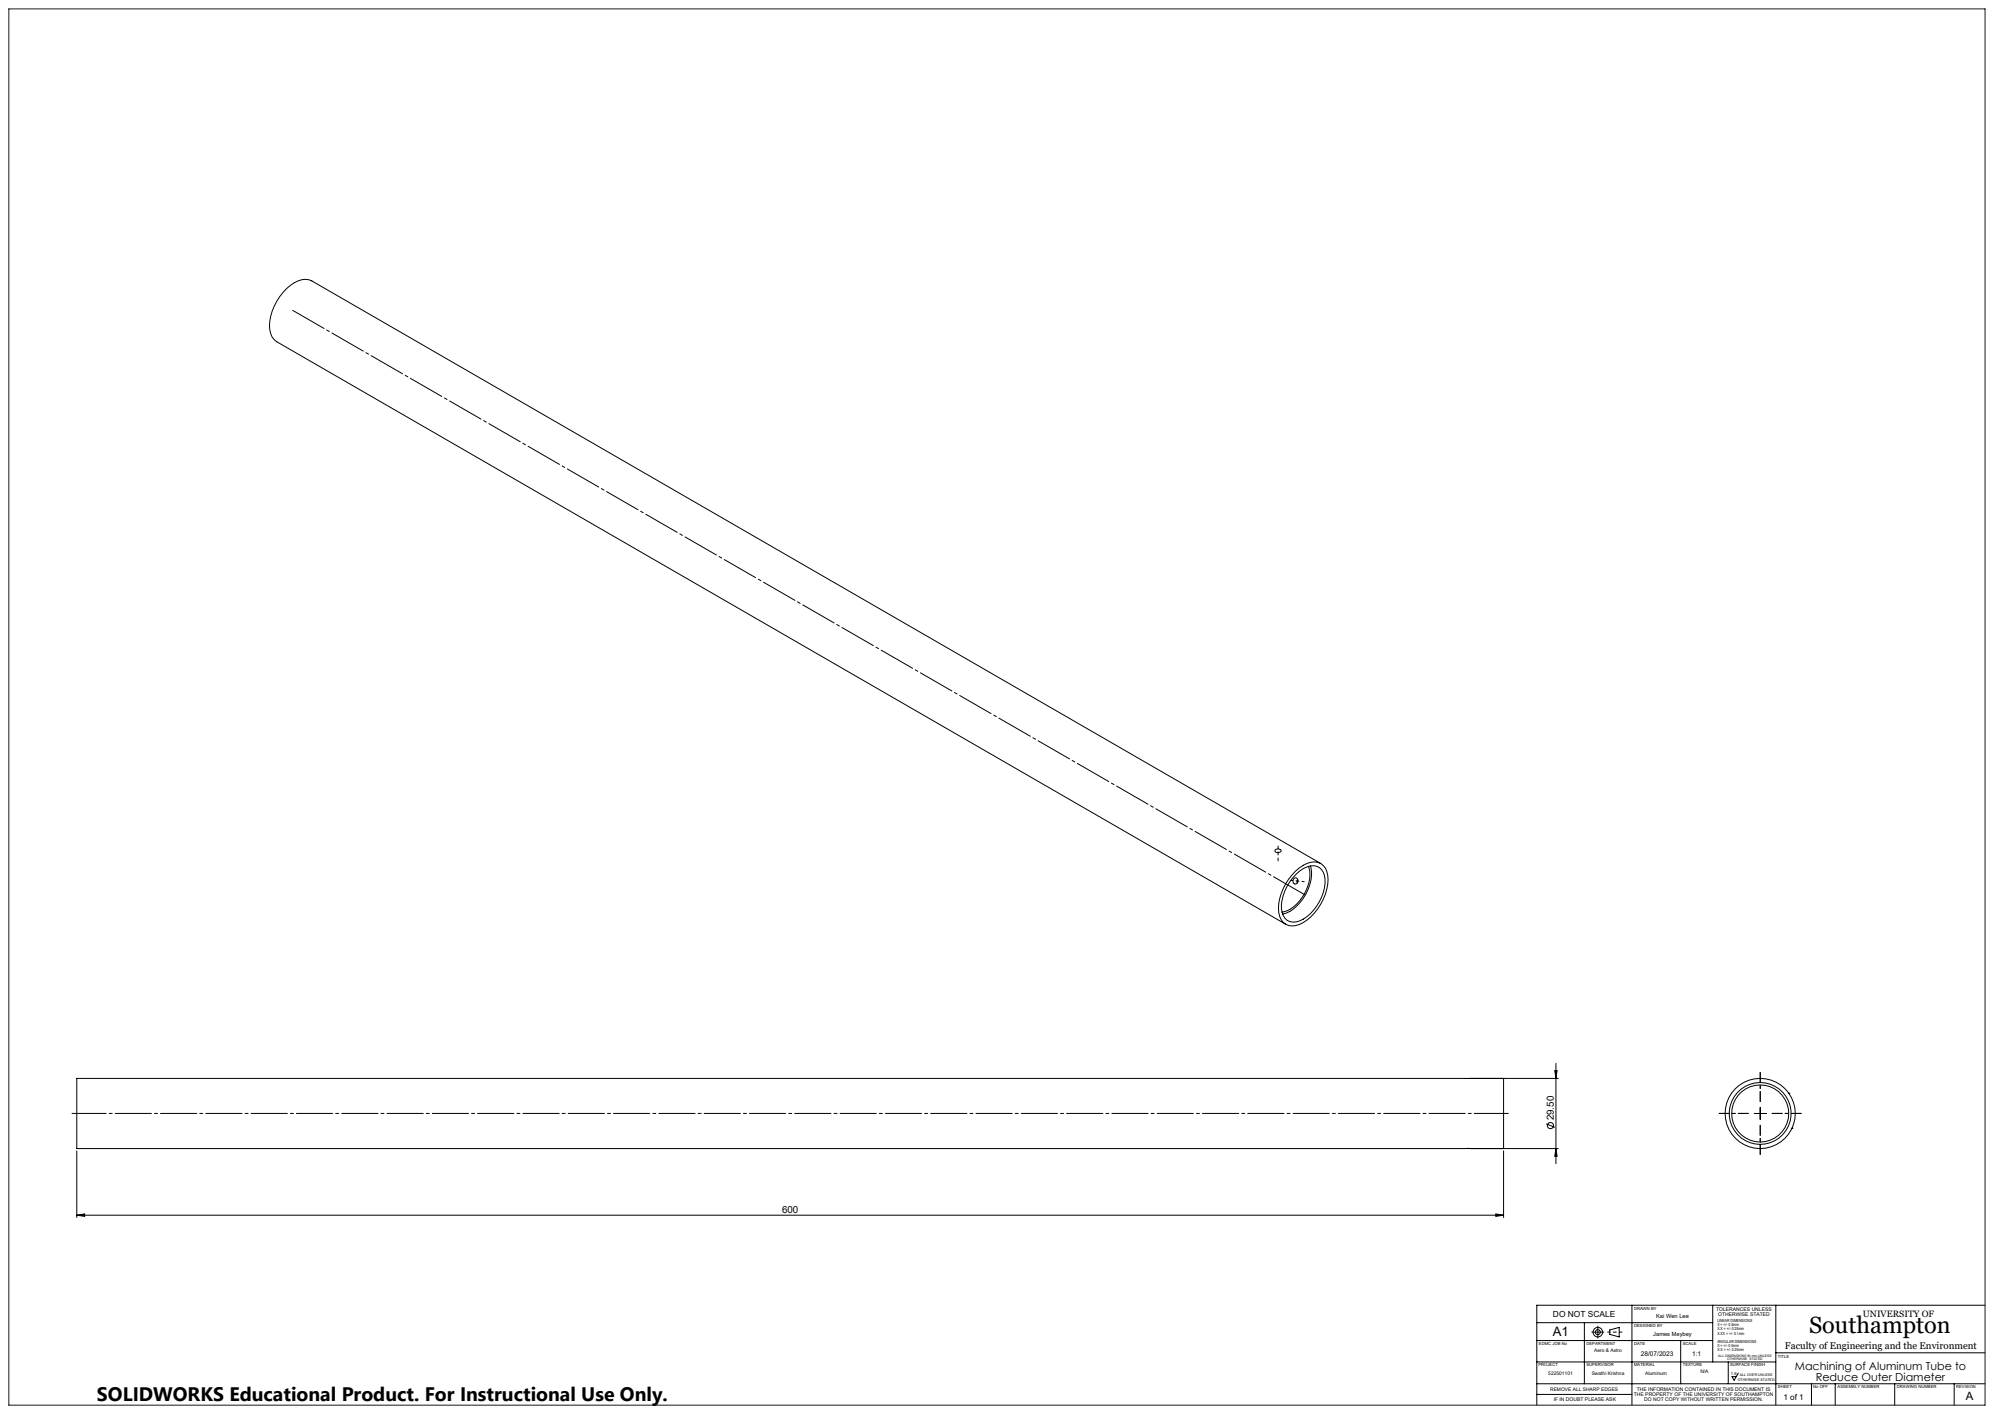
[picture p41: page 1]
Swathi Krishna; Aluminum; Aero & Astro; James Meybey; SHEET; No OFF; ASSEMBLY NUMBER; DRAWING NUMBER; REVISION; PROJECT; SUPERVISOR; MATERIAL; TEXTURE; SURFACE FINISH; TOLERANCES UNLESS OTHERWISE STATED; DESIGNED BY; EDMC JOB No; DEPARTMENT; DATE; SCALE; LINEAR DIMENSIONS X = +/- 0.5mm X.X = +/- 0.25mm X.XX = +/- 0.1mm ANGULAR DIMENSIONS X = +/- 0.5mm; Faculty of Engineering and the Environment

DO NOT SCALE

DRAWN BY
Kai Wen Lee

Southampton UNIVERSITY OF

ALL DIMENSIONS IN mm UNLESS
OTHERWISE STATED

TITLE
Machining of Aluminum Tube to
Reduce Outer Diameter

SOLIDWORKS Educational Product. For Instructional Use Only.

ALL OVER UNLESS

REMOVE ALL SHARP EDGES
IF IN DOUBT PLEASE ASK

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
